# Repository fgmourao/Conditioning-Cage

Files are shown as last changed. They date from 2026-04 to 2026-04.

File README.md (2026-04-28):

# Conditioning Cage v2.0
** Under development

Hardware, firmware and desktop interface for classical fear conditioning.  
Arduino DUE stimulus generator controlled by a Python/PyQt5 application over USB.

---

## Origin

This project is a full rewrite of the system described in:

> Amaral Junior PA, Mourao FAG, Moraes MFD (2019).  
> *A Custom Microcontrolled and Wireless-Operated Chamber for Auditory Fear Conditioning.*  
> Frontiers in Neuroscience.  
> https://doi.org/10.3389/fnins.2019.01193

The original v1.0 architecture used an ESP8266 as a Wi-Fi master communicating with the Arduino DUE via SPI, with a browser-based HTML interface. Version 2.0 removes the ESP8266 entirely — a PyQt5 desktop application communicates directly with the DUE over its native USB port.

Beyond the architectural change, v2.0 introduces several new capabilities: adaptive DAC lookup tables for lower harmonic distortion across the full frequency range, an AM modulation channel with configurable modulator frequency, two independent programmable digital trigger outputs (pins 10 and 11) for synchronising external equipment, an OLED status display, a hardware watchdog with fault detection, and a calibration interface with per-bar shock selection.

---

## Changes from v1.0 to v2.0

### Architecture
The ESP8266 Wi-Fi master and SPI bus are removed entirely. Python communicates directly with the DUE over its native USB port using newline-terminated JSON. All stimulus timing is handled autonomously by the DUE after a single `start` command — no real-time control from the host is required during execution.

### Bug fixes and stability improvements

**Shock clock decoupled from DAC** — in v1.0 the shock interval counter (`iCountShockIntervals`) was incremented inside the `carrier()` ISR, which ran at the DAC rate. Changing `carrier_freq` silently altered shock pulse timing. In v2.0 the shock has its own dedicated Timer6 running at a fixed 10 kHz, completely independent of the DAC.

**Hardware ABORT pin pullup** — in v1.0 `pinABORT` was configured as `INPUT` with no pullup resistor, leaving the pin floating when the button was not pressed and susceptible to spurious aborts from electrical noise. In v2.0 it uses `INPUT_PULLUP`.

**DAC disabled between sounds** — in v1.0 `analogWrite(DAC1, 0)` at sound offset wrote zero but left the DAC channel enabled, injecting DC noise into the amplifier between trials. In v2.0 `dacc_disable_channel` is called at every sound offset and the coupling capacitor is pre-charged to midscale before each onset to eliminate transients.

**Shock pulse timing precision** — in v1.0 `floor()` was used to convert pulse times to tick counts, introducing a systematic downward truncation error. In v2.0 `roundf()` gives the nearest tick (0.1 ms resolution at 10 kHz).

**Watchdog** — v1.0 had no hardware fault detection. If Timer4 or Timer6 stalled, the experiment continued silently with no stimuli. In v2.0 a software watchdog monitors both timers; if either stops incrementing for 5 seconds a fault is declared, all outputs are driven LOW, and the Python interface displays a critical alert.

**DAC buffer type** — in v1.0 the DAC buffer was `uint32_t` (4 bytes per sample), wasting twice the RAM needed. In v2.0 it is `uint16_t` (2 bytes per sample), halving the buffer footprint to 2 KB.

### Sound generation

In v1.0 the carrier lookup table had a fixed 8 samples regardless of frequency. At low carrier frequencies (1–3 kHz) this produced visible harmonic distortion — only 8 points approximated each sine cycle. In v2.0 adaptive tables select 4, 8, 16, or 32 samples based on the carrier frequency, keeping the DAC update rate within the optimal range across the full 0–20 kHz span.

### New stimuli and features

- **LIGHT** — independent light stimulus (pin 45, square wave or DC HIGH) with its own onset, duration, and frequency per trial
- **Trigger 1 / Trigger 2** — two independent digital pulse outputs (pins 10 and 11) for synchronising external equipment, with configurable onset (s) and duration (ms) per trial
- **Baseline period** — quiet time before the first trial, separate from the inter-trial interval
- **Per-trial volume control** — sound amplitude programmable per trial (0–100%)
- **AM modulation** — configurable modulator frequency per trial; `modulator_freq = 0` gives a pure sine
- **OLED status display** — real-time trial state on an SSD1306 128×32 display
- **Bar selection** — calibration mode allows fixing a single shock bar for individual verification
- **Python desktop interface** — replaces the ESP8266 HTML page with a PyQt5 application featuring a trial timeline preview, protocol save/load, event log, and calibration dialogs

---

## Architecture

```
Python / PyQt5  (PC)
      │
      │  SerialUSB — native USB port (USB CDC)
      │
Arduino DUE
      ├─ DAC1         →  Sound  (AM sine, 0–20 kHz)
      ├─ Timer4/5     →  DAC clock / AM modulator ISR
      ├─ Timer6       →  Shock clock (10 kHz)
      ├─ Timer7       →  Light square wave
      ├─ Pins 23–37   →  Shock bars (8 outputs, round-robin)
      ├─ Pin 45       →  Light output
      ├─ Pin 46       →  Watchdog fault output
      ├─ Pin 48       →  Hardware ABORT input
      ├─ Pin 10        →  Trigger 1 output (digital pulse)
      ├─ Pin 11        →  Trigger 2 output (digital pulse)
      ├─ Pins 50–53   →  Sync outputs (SOUND, LIGHT, SHOCK, MOD)
      └─ Pins 20–21   →  I²C — OLED display (SDA / SCL)
```

The DUE stores the complete trial list in RAM and executes the experiment autonomously after a single `start` command. Python is responsible only for programming parameters, triggering execution, and monitoring status.

---

## Stimuli

Five independent stimuli with individual onset and duration per trial:

### Sound
- Output: DAC1 (12-bit, 0–3.3 V)
- Waveform: AM-modulated sine (`SINE_AM`) or pure sine
- Carrier: 0–20 kHz; modulator: 0–500 Hz
- Adaptive lookup tables (see [Sound generation](#sound-generation))
- AC coupling capacitor (10 µF) recommended in series on DAC1 output

### Light
- Output: pin 45, square wave 50% duty cycle
- Frequency: configurable; `light_freq = 9999` = DC HIGH (constant ON)

### Shock
- Outputs: pins 23, 25, 27, 29, 31, 33, 35, 37 (8 bars)
- Round-robin activation or fixed single bar (calibration)
- Pulse HIGH and LOW times configurable in ms (0.1 ms resolution at 10 kHz clock)

### Trigger 1 / Trigger 2
- Outputs: pin 10 (Trigger 1), pin 11 (Trigger 2)
- Simple digital HIGH pulse: onset in seconds, duration in milliseconds
- Independent of each other and of all other stimuli
- Intended for synchronising external equipment (cameras, stimulators, recording systems)

---

## Trial structure

Each trial stores 20 float parameters, transmitted semicolon-separated over serial:

| Field | Description | Unit |
|---|---|---|
| `baseline` | Quiet period before first trial | s |
| `silence` | Inter-trial interval | s |
| `onset_sound` | Sound onset within trial | s |
| `sound_duration` | Sound duration | s |
| `carrier_freq` | DAC carrier frequency; 0 = no sound | Hz |
| `modulator_freq` | AM modulator frequency; 0 = pure sine | Hz |
| `volume` | Sound amplitude | % |
| `waveform_type` | 0 = SINE_AM, 1 = SINE, 2 = SQUARE | — |
| `onset_shock` | Shock onset within trial | s |
| `shock_duration` | Shock duration; 0 = no shock | s |
| `pulse_high` | Shock bar ON time per pulse | ms |
| `pulse_low` | Shock bar OFF time between pulses | ms |
| `onset_light` | Light onset within trial | s |
| `light_duration` | Light duration; 0 = no light | s |
| `light_freq` | Light frequency; 9999 = DC HIGH | Hz |
| `bar_select` | 0 = round-robin, 1–8 = fixed bar | — |
| `onset_trig1` | Trigger 1 onset within trial; 0 = start of trial | s |
| `trig1_duration` | Trigger 1 pulse duration; 0 = disabled | ms |
| `onset_trig2` | Trigger 2 onset within trial; 0 = start of trial | s |
| `trig2_duration` | Trigger 2 pulse duration; 0 = disabled | ms |

---

## Serial protocol

All communication uses newline-terminated JSON objects:

```
{"cmd":"ping"}
    -> {"ok":true,"msg":"pong","version":"2.0"}

{"cmd":"program","n":N,"data":"f0;f1;..."}
    -> {"ok":true,"msg":"N trials programmed"}

{"cmd":"start"}
    -> {"ok":true,"msg":"started"}

{"cmd":"abort"}
    -> {"ok":true,"msg":"aborted"}

{"cmd":"status"}
    -> {"ok":true,"status":N,"trial":N,"total":N,
        "running":bool,"ready":bool,"fault":bool}
```

Status codes: `0` IDLE · `1` READY · `2` RUNNING · `3` DONE · `4` FAULT · `5` ABORTED

---

## Sync outputs

All sync pins are active HIGH while the corresponding stimulus is active.  
**Use these pins as the authoritative timing reference for external equipment** (electrophysiology, cameras). The `onset_*` fields in seconds carry a worst-case jitter of ~500 µs (one loop iteration); the sync pins do not.

| Pin | Signal | Description |
|---|---|---|
| 50 | SOUND_SYN | HIGH while sound is playing |
| 51 | LIGHT_SYN | HIGH while light is active |
| 52 | SHOCK_SYN | HIGH while shock is being delivered |
| 53 | MOD_SYN | Square wave at `modulator_freq`, phase-locked to AM envelope |

---

## OLED status display

Optional SSD1306 128×32 OLED on I²C (SDA = pin 20, SCL = pin 21, address 0x3C).  
Shows experiment state at each transition:

| State | Display |
|---|---|
| Startup | `Conditioning Cage / v2.0 Ready` |
| Trial onset | `TRIAL X/N` / `CS` · `CS + US` · `US` |
| Done | `Conditioning Cage / Done` |
| Aborted | `Conditioning Cage / Aborted` |

The firmware runs normally if the display is not connected.

---

## Sound generation

v2.0 uses adaptive lookup tables (`Waveforms.h`) to minimise harmonic distortion across the full frequency range:

| Carrier frequency | Table size | DAC update rate |
|---|---|---|
| > 10 000 Hz | 4 samples | up to 80 kHz |
| > 3 000 Hz | 8 samples | up to 80 kHz |
| > 1 000 Hz | 16 samples | up to 48 kHz |
| ≤ 1 000 Hz | 32 samples | up to 32 kHz |

All rates are within the SAM3X8E DAC hardware limit of 1 MHz.  
Buffer RAM cost: 32 × 32 × 2 bytes = 2 KB.

AM modulation uses a 32-sample unipolar envelope table. When `modulator_freq = 0` the carrier is output as a pure sine with no modulation.

---

## DAC signal conditioning

The DAC1 output is 0–3.3 V (unipolar). For audio output:

- Place a **10 µF electrolytic capacitor** in series (positive pole toward DAC1) to block DC and pass the AC signal
- Place a **10 kΩ resistor** between the amplifier input and GND to anchor the input when the DAC is disabled
- Use a **potentiometer (10–50 kΩ)** between the capacitor and the amplifier input for level control
- Connect the cable shield to GND on the DUE side only (single-end grounding prevents ground loops)

The firmware disables DAC1 between sounds (`dacc_disable_channel`) and pre-charges the coupling capacitor to midscale before each trial onset to prevent transients.

---

## Python application

### Requirements

```
pip install pyserial PyQt5
```

Python 3.8 or later.

### Features

- Dark/Light-theme PyQt5 desktop application
- Trial configuration panel: per-stimulus onset, duration, frequency, volume, pulse timing, trigger durations
- Recorded trials table with per-row delete
- Timeline preview: block diagram of all trials on a shared time axis with a real-time progress line during execution; rows are shown only for stimuli with non-zero duration
- Event log with timestamps (`YYYY-MM-DD HH:MM:SS`) — exportable via Save Log
- **Protocol menu:** Save Protocol, Load Protocol, Clear All Trials, Save Log
- **Calibration menu:** Sound, Light, Shock — continuous single-trial stimulus stopped by ABORT; shock calibration allows bar selection and configurable pulse timing
- **Help menu:** Info dialog
- Port selector with refresh button
- 4-second timeout warning if DUE does not respond after connection
- Firmware version check on connect (warns if not v2.0)
- Watchdog fault popup with critical alert
- Hardware ABORT button (pin 48) is read inside the trial timing loop and during inter-trial silences — responsive at any point during experiment execution

### Poll strategy

The poll timer (`{"cmd":"status"}` every 1500 ms) is stopped when the experiment starts to prevent USB interrupt collisions with Timer4 on the Native Port. One poll is scheduled at the calculated onset of each trial using `QTimer.singleShot`. A generation counter invalidates scheduled polls that remain pending after an ABORT. The poll timer resumes when the experiment ends or is aborted.

---

## Hardware requirements

| Component | Specification |
|---|---|
| Microcontroller | Arduino DUE |
| USB connection | Native port (second USB connector) |
| Shock bars | 8 outputs — pins 23, 25, 27, 29, 31, 33, 35, 37 |
| Light output | Pin 45 |
| Trigger 1 output | Pin 10 — digital pulse |
| Trigger 2 output | Pin 11 — digital pulse |
| ABORT button | Momentary switch — pin 48 to GND |
| DAC coupling | 10 µF electrolytic capacitor in series on DAC1 |
| Amplifier | Class-D module (e.g. TDA8932); 10–50 kΩ potentiometer at input |
| Speaker | Tweeter (2–20 kHz); 4 Ω or 8 Ω |
| OLED (optional) | SSD1306 128×32, I²C, address 0x3C |

---

## Files

| File | Description |
|---|---|
| `cage_app_dark.py` | Main application — dark theme |
| `Stimuli_PY_DUE.ino` | Arduino DUE firmware |
| `Waveforms.h` | Adaptive DAC lookup tables |
| `image.png` | Logo displayed in the application header |

Arduino library dependencies (install via Arduino IDE Library Manager):
- **DueTimer** (Ivan Seidel)
- **Adafruit GFX Library**
- **Adafruit SSD1306**

---

## Known limitations

- Noise waveforms (white, pink) are not implemented. The lookup-table architecture is periodic; a possible approach is to generate noise buffers in Python (NumPy/SciPy) and send them as custom tables over serial.
- If the USB cable is disconnected during an experiment, the DUE continues executing autonomously. The only way to stop it is the hardware ABORT button (pin 48).

---

## License

Documentation licensed under Creative Commons Attribution-NonCommercial 4.0 International (CC BY-NC 4.0).

---

## Authors

**v1.0 (2019)**  
Paulo Aparecido Amaral Junior, Flavio Afonso Goncalves Mourao, Marcio Flavio Dutra Moraes  
*Núcleo de Neurociências, Federal University of Minas Gerais, Brazil*

**v2.0 (2026)**  
Flavio Afonso Goncalves Mourao — [mourao.fg@gmail.com](mailto:mourao.fg@gmail.com)  
*CNPq/MCTI/FNDCT Nº 21/2024 — Processo 446467/2024-3*  
*Federal University of Minas Gerais, Brazil*

---

*Last update: April 2026*

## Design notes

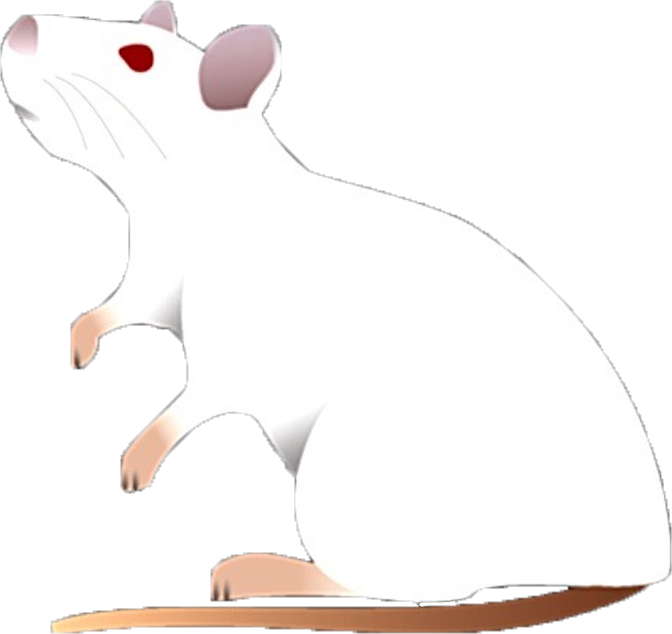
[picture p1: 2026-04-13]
Firmware/PY_software/image.png

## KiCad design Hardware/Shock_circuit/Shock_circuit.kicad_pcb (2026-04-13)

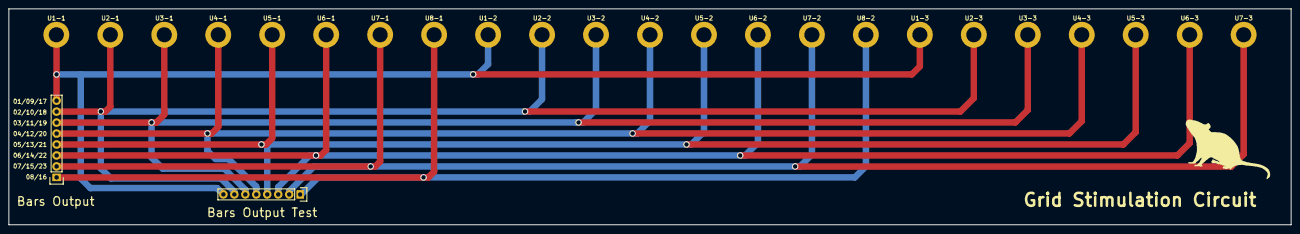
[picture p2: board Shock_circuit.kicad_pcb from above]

Board: 2 copper layers, 297.0 x 50.0 mm, 25 parts (0 on the bottom side), 8 nets.

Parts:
P1: Bars Output Test; Pin_Header_Straight_1x08
P2: Bars Output; Pin_Header_Straight_1x08
U1-1, U1-2, U1-3, U2-1, U2-2, U2-3, U3-1, U3-2, U3-3, U4-1, U4-2, U4-3, U5-1, U5-2, U5-3, U6-1, U6-2, U6-3, U7-1, U7-2, U7-3, U8-1, U8-2: Bar_Hole

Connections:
/InBarra1: P1.8, P2.8, U1-1.1, U1-2.1, U1-3.1
/InBarra2: P1.7, P2.7, U2-1.1, U2-2.1, U2-3.1
/InBarra3: P1.6, P2.6, U3-1.1, U3-2.1, U3-3.1
/InBarra4: P1.5, P2.5, U4-1.1, U4-2.1, U4-3.1
/InBarra5: P1.4, P2.4, U5-1.1, U5-2.1, U5-3.1
/InBarra6: P1.3, P2.3, U6-1.1, U6-2.1, U6-3.1
/InBarra7: P1.2, P2.2, U7-1.1, U7-2.1, U7-3.1
/InBarra8: P1.1, P2.1, U8-1.1, U8-2.1

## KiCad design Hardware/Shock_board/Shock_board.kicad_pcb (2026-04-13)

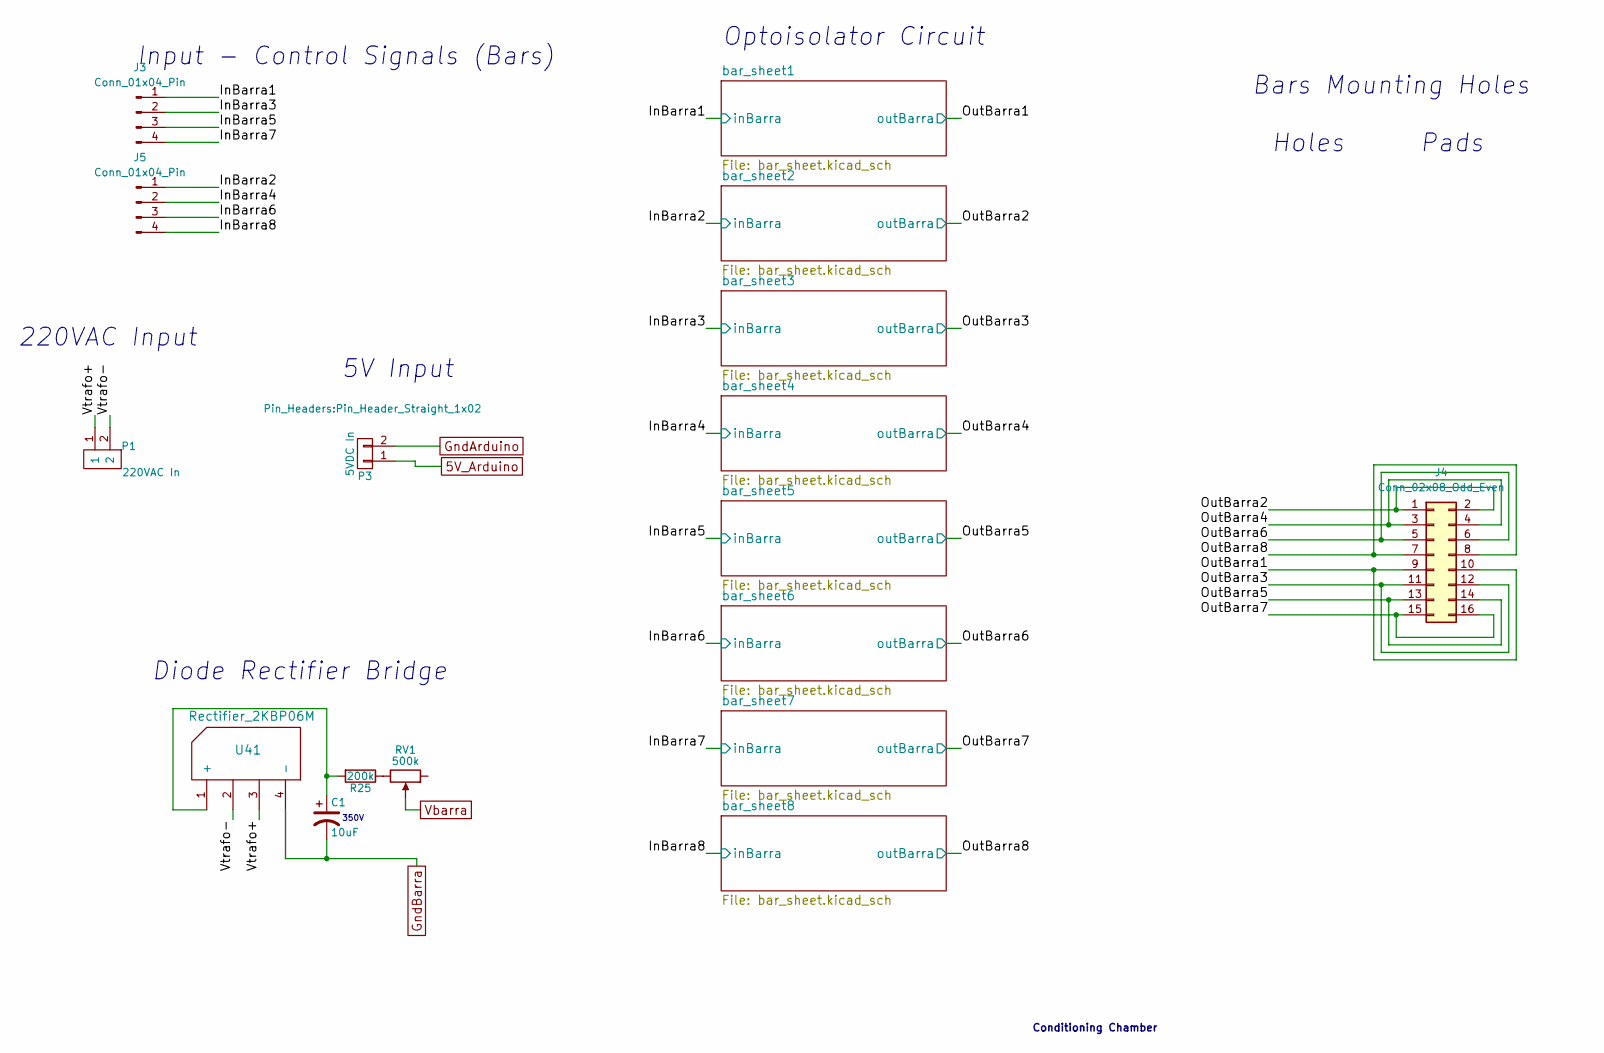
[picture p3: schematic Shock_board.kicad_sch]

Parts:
C1: 10uF; CP_Radial_D10.0mm_P7.50mm
J3: Conn_01x04_Pin; PinHeader_1x04_P2.54mm_Vertical
J4: Conn_02x08_Odd_Even; IDC-Header_2x08_P2.54mm_Vertical
J5: Conn_01x04_Pin; PinSocket_1x04_P2.54mm_Vertical
P1: 220VAC In; Pin_Header_Straight_1x02_Pitch2.54mm
P3: 5VDC In; Pin_Header_Straight_1x02
R25: 200k; R_Axial_DIN0207_L6.3mm_D2.5mm_P10.16mm_Horizontal
RV1: 500k; Potentiometer_Alps_RK163_Single_Vertical
U41: Rectifier_2KBP06M

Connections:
5V_Arduino: P3.1; also elsewhere on the board
/Vtrafo+: P1.1, U41.3
/Vtrafo-: P1.2, U41.2
GndArduino: P3.2; also elsewhere on the board
GndBarra: C1.2, U41.4 (-); also elsewhere on the board
unnamed: J4.1, J4.2
unnamed: J4.3, J4.4
unnamed: J4.5, J4.6
unnamed: J4.7, J4.8
unnamed: J4.9, J4.10
unnamed: J4.11, J4.12
unnamed: J4.13, J4.14
unnamed: J4.15, J4.16
unnamed 53: R25.1, RV1.3; also elsewhere on the board
unnamed: C1.1, R25.2, U41.1 (+)

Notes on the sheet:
350V
Input - Control Signals (Bars)
Diode Rectifier Bridge
220VAC Input
Bars Mounting Holes
Optoisolator Circuit
5V Input
Holes
Conditioning Chamber
Pads

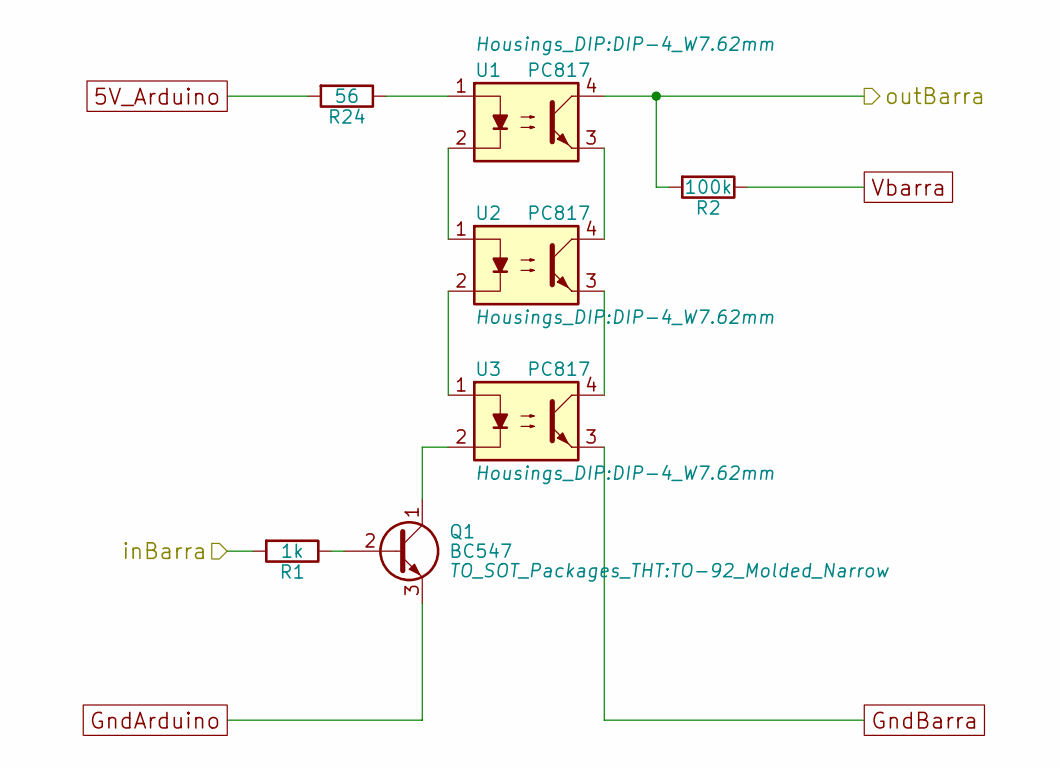
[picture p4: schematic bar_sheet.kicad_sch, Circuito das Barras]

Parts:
Q1: BC547; TO-92_Molded_Narrow
R1: 1k; R_Axial_DIN0207_L6.3mm_D2.5mm_P10.16mm_Horizontal
R2: 100k; R_Axial_DIN0411_L9.9mm_D3.6mm_P5.08mm_Vertical
R24: 56; R_Axial_DIN0207_L6.3mm_D2.5mm_P10.16mm_Horizontal
U1, U2, U3: PC817; DIP-4_W7.62mm

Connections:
5V_Arduino: R24.2; also elsewhere on the board
/InBarra1: R1.2; also elsewhere on the board
/OutBarra1: R2.2, U1.4; also elsewhere on the board
GndArduino: Q1.3 (E); also elsewhere on the board
GndBarra: U3.3; also elsewhere on the board
unnamed: Q1.2 (B), R1.1
unnamed: Q1.1 (C), U3.2
unnamed: R24.1, U1.1
unnamed: U1.2, U2.1
unnamed: U1.3, U2.4
unnamed: U2.2, U3.1
unnamed: U2.3, U3.4
Vbarra: R2.1; also elsewhere on the board

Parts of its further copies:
Q2, Q3, Q4, Q5, Q6, Q7, Q8: BC547; TO-92_Molded_Narrow
R3, R5, R7, R9, R11, R13, R15: 1k; R_Axial_DIN0207_L6.3mm_D2.5mm_P10.16mm_Horizontal
R4, R6, R8, R10, R12, R14, R16: 100k; R_Axial_DIN0411_L9.9mm_D3.6mm_P5.08mm_Vertical
R17, R18, R19, R20, R21, R22, R23: 56; R_Axial_DIN0207_L6.3mm_D2.5mm_P10.16mm_Horizontal
U4, U5, U6, U7, U8, U9, U10, U11, U12, U13, U14, U15, U16, U17, U18, U19, U20, U21, U22, U23, U24: PC817; DIP-4_W7.62mm

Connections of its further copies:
5V_Arduino: R17.2, R18.2, R19.2, R20.2, R21.2, R22.2, R23.2; also elsewhere on the board
/InBarra2: R3.2; also elsewhere on the board
/InBarra3: R5.2; also elsewhere on the board
/InBarra4: R7.2; also elsewhere on the board
/InBarra5: R9.2; also elsewhere on the board
/InBarra6: R11.2; also elsewhere on the board
/InBarra7: R13.2; also elsewhere on the board
/InBarra8: R15.2; also elsewhere on the board
/OutBarra2: R4.2, U4.4; also elsewhere on the board
/OutBarra3: R6.2, U7.4; also elsewhere on the board
/OutBarra4: R8.2, U10.4; also elsewhere on the board
/OutBarra5: R10.2, U13.4; also elsewhere on the board
/OutBarra6: R12.2, U16.4; also elsewhere on the board
/OutBarra7: R14.2, U19.4; also elsewhere on the board
/OutBarra8: R16.2, U22.4; also elsewhere on the board
GndArduino: Q2.3 (E), Q3.3 (E), Q4.3 (E), Q5.3 (E), Q6.3 (E), Q7.3 (E), Q8.3 (E); also elsewhere on the board
GndBarra: U6.3, U9.3, U12.3, U15.3, U18.3, U21.3, U24.3; also elsewhere on the board
unnamed: Q2.2 (B), R3.1
unnamed: Q2.1 (C), U6.2
unnamed: Q3.2 (B), R5.1
unnamed: Q3.1 (C), U9.2
unnamed: Q4.2 (B), R7.1
unnamed: Q4.1 (C), U12.2
unnamed: Q5.2 (B), R9.1
unnamed: Q5.1 (C), U15.2
unnamed: Q6.2 (B), R11.1
unnamed: Q6.1 (C), U18.2
unnamed: Q7.2 (B), R13.1
unnamed: Q7.1 (C), U21.2
unnamed: Q8.2 (B), R15.1
unnamed: Q8.1 (C), U24.2
unnamed: R17.1, U7.1
unnamed: R18.1, U10.1
unnamed: R19.1, U13.1
unnamed: R20.1, U16.1
unnamed: R21.1, U19.1
unnamed: R22.1, U22.1
unnamed: R23.1, U4.1
unnamed: U4.2, U5.1
unnamed: U4.3, U5.4
unnamed: U5.2, U6.1
unnamed: U5.3, U6.4
unnamed: U7.2, U8.1
unnamed: U7.3, U8.4
unnamed: U8.2, U9.1
unnamed: U8.3, U9.4
unnamed: U10.2, U11.1
unnamed: U10.3, U11.4
unnamed: U11.2, U12.1
unnamed: U11.3, U12.4
unnamed: U13.2, U14.1
unnamed: U13.3, U14.4
unnamed: U14.2, U15.1
unnamed: U14.3, U15.4
unnamed: U16.2, U17.1
unnamed: U16.3, U17.4
unnamed: U17.2, U18.1
unnamed: U17.3, U18.4
unnamed: U19.2, U20.1
unnamed: U19.3, U20.4
unnamed: U20.2, U21.1
unnamed: U20.3, U21.4
unnamed: U22.2, U23.1
unnamed: U22.3, U23.4
unnamed: U23.2, U24.1
unnamed: U23.3, U24.4
Vbarra: R4.1, R6.1, R8.1, R10.1, R12.1, R14.1, R16.1; also elsewhere on the board

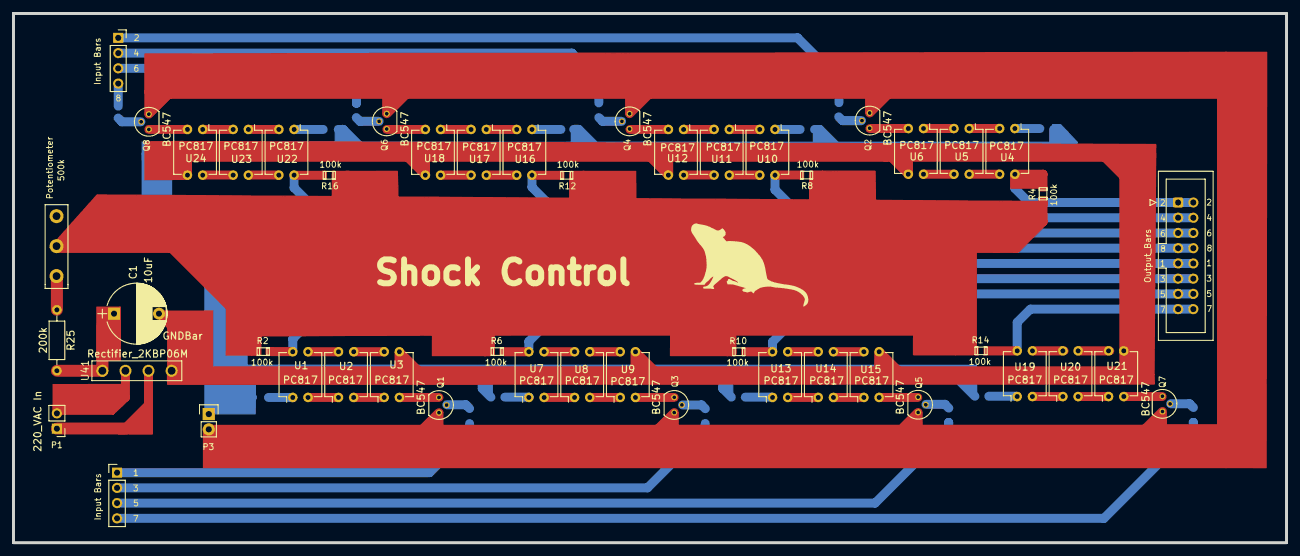
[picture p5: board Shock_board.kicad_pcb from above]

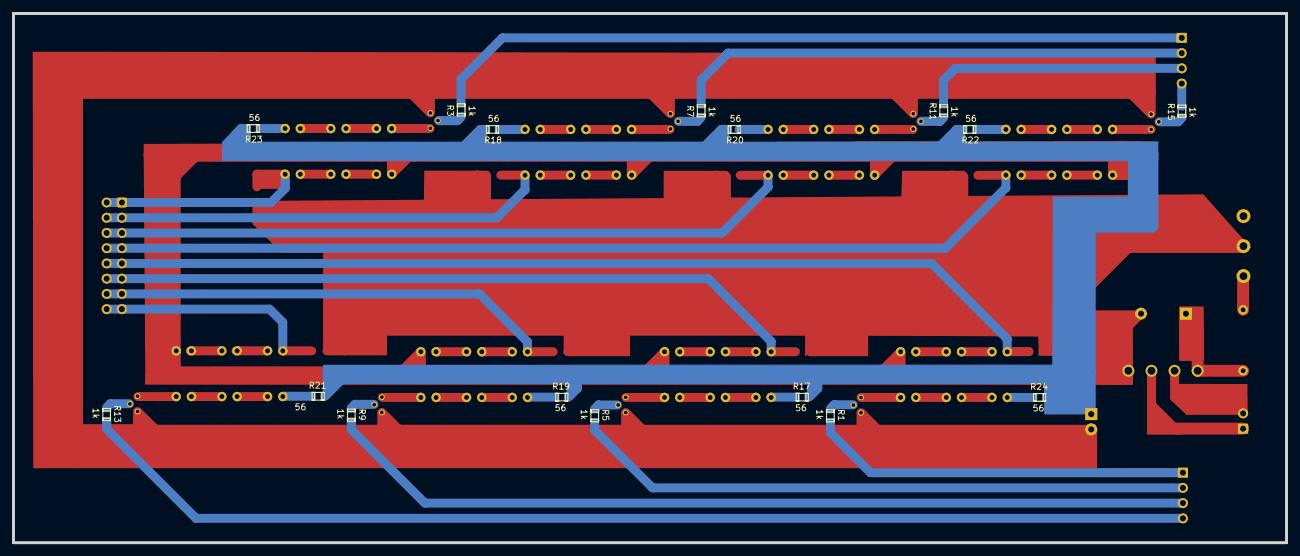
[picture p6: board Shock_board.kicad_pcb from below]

Board: 2 copper layers, 212.3 x 88.3 mm, 65 parts (16 on the bottom side), 80 nets.

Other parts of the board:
Input Bars: PinHeader_1x04_P2.54mm_Vertical
Input Bars#2: PinSocket_1x04_P2.54mm_Vertical
Output_Bars: IDC-Header_2x08_P2.54mm_Vertical
Potentiometer: 500k; Potentiometer_Alps_RK163_Single_Vertical

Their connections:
/InBarra1: Input Bars.1; also elsewhere on the board
/InBarra2: Input Bars#2.1; also elsewhere on the board
/InBarra3: Input Bars.2; also elsewhere on the board
/InBarra4: Input Bars#2.2; also elsewhere on the board
/InBarra5: Input Bars.3; also elsewhere on the board
/InBarra6: Input Bars#2.3; also elsewhere on the board
/InBarra7: Input Bars.4; also elsewhere on the board
/InBarra8: Input Bars#2.4; also elsewhere on the board
/OutBarra1: Output_Bars.9, Output_Bars.10; also elsewhere on the board
/OutBarra2: Output_Bars.1, Output_Bars.2; also elsewhere on the board
/OutBarra3: Output_Bars.11, Output_Bars.12; also elsewhere on the board
/OutBarra4: Output_Bars.3, Output_Bars.4; also elsewhere on the board
/OutBarra5: Output_Bars.13, Output_Bars.14; also elsewhere on the board
/OutBarra6: Output_Bars.5, Output_Bars.6; also elsewhere on the board
/OutBarra7: Output_Bars.15, Output_Bars.16; also elsewhere on the board
/OutBarra8: Output_Bars.7, Output_Bars.8; also elsewhere on the board
unnamed 53: Potentiometer.3; also elsewhere on the board
Vbarra: Potentiometer.2; also elsewhere on the board

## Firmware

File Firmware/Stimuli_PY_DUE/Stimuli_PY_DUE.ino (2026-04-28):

/* Stimuli_PY_DUE.ino
 *
 * PROJECT : Conditioning Cage
 * Arduino DUE stimulus generator for classical fear conditioning.
 * Version: 2.0
 *
 * Architecture:
 *   Controlled entirely via the SerialUSB native port (Python on PC).
 *   Note: SerialUSB.begin(115200) is called for completeness but the baudrate
 *   parameter is ignored on the Native Port -- USB CDC always runs at USB speed.
 *   The DUE stores the complete trial list in RAM and executes the experiment
 *   autonomously after receiving a START command. Python manages timing only
 *   at the experiment level (sending parameters and start/abort); all stimulus
 *   onset/offset timing is handled by the DUE using micros() at 500 us resolution.
 *
 * Sound generation (Waveforms.h adaptive lookup tables):
 *   carrier_freq >  10000 Hz:  4-sample table  (DAC Timer4 rate up to  80 kHz)
 *   carrier_freq >   3000 Hz:  8-sample table  (DAC Timer4 rate up to  80 kHz)
 *   carrier_freq >   1000 Hz: 16-sample table  (DAC Timer4 rate up to  48 kHz)
 *   carrier_freq <=  1000 Hz: 32-sample table  (DAC Timer4 rate up to  32 kHz)
 *   All rates are within the SAM3X8E DAC hardware limit of 1 MHz.
 *   Modulator: fixed 32-sample unipolar [0,1] table. Timer5 rate = modulator_freq x 32.
 *   modulator_freq = 0: pure carrier sine, no AM modulation.
 *   Waveform types: SINE_AM (0), SINE (1), SQUARE (2).
 *                   NOTE (v2.0): SINE and SQUARE are implemented in firmware but currently
 *                   unused. The Python UI always sends waveform_type=0 (SINE_AM), which
 *                   falls back to pure sine when modulator_freq=0. SINE/SQUARE remain
 *                   available via manual protocol edit and may be re-enabled in a future UI release. 
 * Five independent stimuli with individual onset/offset timing:
 *   SOUND    -- DAC1, AM sine or pure sine or square wave, Timer4/Timer5
 *   SHOCK    -- 8 bar pins round-robin, Timer6 at 10 kHz clock
 *   LIGHT    -- pin 45, square wave 50% duty cycle, Timer7
 *   TRIGGER1 -- pin 10, digital HIGH pulse, duration in ms
 *   TRIGGER2 -- pin 11, digital HIGH pulse, duration in ms
 *
 * OLED status display (128x32, SSD1306, I2C address 0x3C):
 *   Wired to DUE I2C bus: SDA = pin 20, SCL = pin 21.
 *   Shows experiment state at each transition:
 *     Startup  : "Conditioning Cage / v2.0  Ready."
 *     Trial    : "TRIAL X/N / CS"  or  "CS + US"  or  "US"
 *     Done     : "Conditioning Cage / Done"
 *     Aborted  : "Conditioning Cage / Aborted"
 *   Updated in RunTrial() before ProgramSound() -- no audio glitch risk.
 *   sendStatus() is also called at the same point to notify Python of trial onset.
 *
 * SerialUSB protocol (newline-terminated JSON, USB CDC speed):
 *   {"cmd":"ping"}                              -> {"ok":true,"msg":"pong","version":"2.0"}
 *   {"cmd":"status"}                            -> {"ok":true,"status":N,"trial":N,...}
 *   {"cmd":"program","n":N,"data":"f0;f1;..."}  -> {"ok":true,"msg":"N trials programmed"}
 *   {"cmd":"start"}                             -> {"ok":true,"msg":"started"}
 *   {"cmd":"abort"}                             -> {"ok":true,"msg":"aborted"}
 *
 *   program data format: N x FIELDS_PER_TRIAL floats, semicolon-separated, row-major.
 *   Field order per trial: baseline, silence, onset_sound, sound_duration, carrier_freq,
 *   modulator_freq, volume, waveform_type, onset_shock, shock_duration, pulse_high,
 *   pulse_low, onset_light, light_duration, light_freq, bar_select,
 *   onset_trig1, trig1_duration, onset_trig2, trig2_duration.
 *
 * Sync outputs (all active HIGH while the corresponding stimulus is active):
 *   pin 50 -- SOUND_SYN  sound active
 *   pin 51 -- LIGHT_SYN  light active
 *   pin 52 -- SHOCK_SYN  shock active
 *   pin 53 -- MOD_SYN    square wave at modulator_freq (phase-locked to AM envelope)
 *
 *   TIMING REFERENCE: the sync pins are driven at the exact moment of stimulus
 *   onset/offset inside the RunTrial() timing loop. Use these pins as the
 *   timing reference for external equipment (electrophysiology,
 *   cameras, etc.). The onset_* fields in seconds have a worst-case jitter of
 *   ~500 us (one loop iteration) and ~250 us typical.
 *
 * Pin assignments:
 *   DAC1 -- sound output (12-bit, 0-3.3V)
 *   45   -- light stimulus output (square wave, 50% duty)
 *   46   -- watchdog fault output (HIGH pulse on fault)
 *   48   -- hardware ABORT input (INPUT_PULLUP, active LOW)
 *   13   -- debug LED (ON when parameters received OK, OFF after abort)
 *   20   -- I2C SDA (OLED display)
 *   21   -- I2C SCL (OLED display)
 *   10   -- Trigger 1 output (HIGH during trig1_duration ms after onset_trig1)
 *   11   -- Trigger 2 output (HIGH during trig2_duration ms after onset_trig2)
 *   23,25,27,29,31,33,35,37 -- shock bar outputs (active HIGH, round-robin)
 *
 * Timer allocation:
 *   Timer4 -- carrier()    ISR: writes DACbuffer samples to DAC1
 *   Timer5 -- modulating() ISR: advances modulator index, drives MOD_SYN
 *   Timer6 -- shockClock() ISR: 10 kHz shock bar timing clock
 *   Timer7 -- lightClock() ISR: light square wave toggle
 *
 * Based on Version 1.0 (2019): ESP8266 WiFi master + Arduino DUE SPI slave architecture.
 *   Authors: Paulo Aparecido Amaral Junior, Flavio Afonso Goncalves Mourao, Marcio Flavio Dutra Moraes
 *            Nucleo de Neurociencias UFMG/Brazil
 *            https://doi.org/10.3389/fnins.2019.01193
 *
 * Version 2.0 (2026)
 * Author:  Flavio Afonso Goncalves Mourao  mourao.fg@gmail.com
 */

#include "DueTimer.h"
#include "Waveforms.h"
#include <Wire.h>
#include <Adafruit_GFX.h>
#include <Adafruit_SSD1306.h>

#define SCREEN_WIDTH  128
#define SCREEN_HEIGHT  32
Adafruit_SSD1306 display(SCREEN_WIDTH, SCREEN_HEIGHT, &Wire, -1);

/*############################################################################################################
        Constants
############################################################################################################*/

// Maximum number of trials stored in RAM.
// Increasing this also requires increasing sbuf (see sizing table below).
#define MAX_TRIALS          100

// Number of float fields per trial (must match Python FIELDS list).
#define FIELDS_PER_TRIAL    20

// SAM3X8E hardware DAC update rate limit: 1 MHz.
// Timer4 frequency = carrier_freq x nC must not exceed this value.
#define DAC_MAX_RATE        1000000.0f

// Timer6 runs at this fixed frequency to clock the shock bar state machine.
// Resolution: 1 / SHOCK_CLOCK_HZ = 0.1 ms per tick.
// pulse_high and pulse_low (ms) are converted to tick counts in ProgramShock().
#define SHOCK_CLOCK_HZ      10000.0f

// Watchdog: if Timer4 or Timer6 stops incrementing for this long, trigger a fault.
#define WATCHDOG_TIMEOUT_MS 5000UL

// Duration of the fault pulse on pinERROR (ms).
#define WATCHDOG_PULSE_MS   200UL

// Waveform type identifiers (stored as float in Trial struct, cast to int in ProgramSound).
// NOTE: SINE and SQUARE are functional but not exposed in the current Python UI.
// All trials from cage_app.py currently send waveform_type = WAVE_SINE_AM.
#define WAVE_SINE_AM  0  // AM-modulated sine: carrier amplitude follows modulator envelope
#define WAVE_SINE     1  // Pure sine: no AM, modulator table ignored (not used by UI)
#define WAVE_SQUARE   2  // Square wave: DAC alternates between 0 and 4095*vol (not used by UI)

// Experiment status codes returned in JSON status responses.
#define ST_IDLE    0  // Waiting for parameters
#define ST_READY   1  // Parameters received, ready to start
#define ST_RUNNING 2  // Experiment in progress
#define ST_DONE    3  // All trials completed normally
#define ST_FAULT   4  // Watchdog fault detected, experiment aborted
#define ST_ABORTED 5  // Aborted by Python command or hardware button

/*############################################################################################################
        Pin assignments
############################################################################################################*/

// Hardware ABORT button: INPUT_PULLUP, active LOW.
// Connects between pin 48 and GND. Triggers immediate Abort() when pressed.
static const int pinABORT      = 48;
// Sync outputs: driven HIGH at stimulus onset, LOW at offset.
// Used for external recording synchronisation (e.g. electrophysiology, camera trigger).
static const int pinSOUND_SYN  = 50;
static const int pinSHOCK_SYN  = 52;
static const int pinLIGHT_SYN  = 51;
// Modulator sync: square wave at modulator_freq, phase-locked to the AM envelope.
// Transitions at iM==0 (LOW) and iM==MOD_SAMPLES_WF/2 (HIGH) inside modulating() ISR.
// Useful for locking external equipment to the AM cycle.
static const int pinMOD_SYN    = 53;
// Light stimulus output: square wave at light_freq, 50% duty cycle, driven by Timer7.
static const int pinLIGHT      = 45;
// Watchdog fault indicator: HIGH pulse of WATCHDOG_PULSE_MS on timer fault.
static const int pinERROR      = 46;
// Debug Light: ON when trial parameters are loaded, OFF after Abort().
static const int pinLIGHT_DBG  = 13;

// Trigger outputs: driven HIGH at onset, LOW at offset.
// Independent programmable digital pulses for synchronising external equipment.
static const int pinTRIG1      = 10;
static const int pinTRIG2      = 11;

// Shock bar pins: 8 pins starting at iInitialBar, spaced by barStep.
// Round-robin activation: one bar active at a time, advancing each pulse cycle.
static const int iInitialBar   = 23;
static const int nBars         = 8;
static const int barStep       = 2;
/*############################################################################################################
        Trial structure
        Each field is stored as float for uniform SerialUSBisation.
        Times are in seconds; frequencies in Hz; volume in %; pulse times in ms.
############################################################################################################*/

struct Trial {
  float baseline;        // Baseline period before first trial starts (s)
  float silence;         // Inter-trial silence before this trial starts (s)
  float onset_sound;     // Sound onset time within trial (s), relative to trial start
  float sound_duration;  // Sound duration (s)
  float carrier_freq;    // DAC carrier frequency (Hz); 0 = no sound
  float modulator_freq;  // AM modulator frequency (Hz); 0 = pure sine
  float volume;          // Sound amplitude (%), 0-100
  float waveform_type;   // 0=SINE_AM, 1=SINE, 2=SQUARE (cast to int in ProgramSound). Python UI always sends 0; SINE/SQUARE reserved for future use.
  float onset_shock;     // Shock onset time within trial (s)
  float shock_duration;  // Shock duration (s); 0 = no shock
  float pulse_high;      // Shock bar ON time per pulse (ms)
  float pulse_low;       // Shock bar OFF time between pulses (ms)
  float onset_light;     // Light onset time within trial (s)
  float light_duration;  // Light duration (s); 0 = no light
  float light_freq;      // Light square wave frequency (Hz); 9999 = DC HIGH (constant ON)
  float bar_select;      // Shock bar selection: 0 = round-robin (default), 1-8 = fixed bar
  float onset_trig1;     // Trigger 1 onset time within trial (s)
  float trig1_duration;  // Trigger 1 pulse duration (ms); 0 = disabled
  float onset_trig2;     // Trigger 2 onset time within trial (s)
  float trig2_duration;  // Trigger 2 pulse duration (ms); 0 = disabled
};

// Trial list stored in SRAM.
// Loaded by handleSerialUSB() on "program" command.
Trial   trials[MAX_TRIALS];
int     nTrials      = 0;     // Number of trials currently programmed
int     currentTrial = 0;     // Index of the trial currently executing (0-based)
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
